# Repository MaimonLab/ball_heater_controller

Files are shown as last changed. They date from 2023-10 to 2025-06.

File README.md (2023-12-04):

# Ball Heater Controller

This repo contains the schematics and associated code for a controller to control the temperature of a ball holder or other device using closed loop PID drive of a resistive heater. There is a Python class to interact with the controller over USB-Serial, as well as a ROS2 Node to send and receive commands with the controller using ROS2.

For instructions on building a Ball Heater Controller, see [Assembly.](docs/assembly.md)

## Basic Usage

The Ball Heater Controller can be used independently of a computer by simply supplying it with AC power and attaching a ball heater and thermistor assembly to the main 4 pin output port on the front.

You can then change the mode by pressing and holding the control knob (see [Modes](#controller-modes)), and set the temperature setpoint (shown lower left as `SP:` on the LCD) by turning the knob. Current temperature is shown bottom right on the LCD.

### Python

The device can also be used with a computer for greater control and temperature logging. Interaction is done over USB-Serial, and the computer side is managed through the `BallHeaterDriver` Python class found in [`ball_heater_driver.py`](ball_heater_controller/ball_heater_controller/ball_heater_driver.py). An example of how this class can be used can be found in the Jupyter Notebook [`ball_heater_controller_testing.ipynb`](ball_heater_controller/ball_heater_controller/ball_heater_controller_testing.ipynb)

In short, after creating a `BallHeaterDriver` object, providing the correct serial port, commands can be sent using the `send_command` method. The main commands you will use are `status`, `set_target_temp`, and `set_control_mode`. Valid syntax for creating an object and sending these commands is shown below, with the first valid serial port chosen by default.

```python
import ball_heater_driver 
from list_ports import list_ports
import time

ports = [
    port
    for port in list_ports()
    if port["manufacturer"] is not None and "Silicon Labs" in port["manufacturer"]
]
port = ports[0]["port"]
print(f"Using Port: {port}")
ball_heater = ball_heater_driver.BallHeaterDriver(port=port)

# wait for the device to reset
time.sleep(5)

# Get and print status
success, status = ball_heater.send_command('status', [])
print('current status is:')
print('\n'.join((f"{key} : {value}") for key, value in status.items()))

# Set the target temperature to 35 (will also set control mode to remote)
ball_heater.send_command("set_target_temp", [35])

# Set the control mode back to standby
ball_heater.send_command("set_control_mode", ["standby"])
```

### ROS2

There is also a ROS2 Node provided for interacting with the Ball Heater Controller, [`ball_heater_node.py`](ball_heater_controller/ball_heater_controller/ball_heater_node.py).  The launch file [example_ball_heater.launch.py](ball_heater_controller/launch/example_ball_heater.launch.py), along with the config file [example_config.yaml](ball_heater_controller/config/example_config.yaml) will launch the node, as well as an example client node that can interact with the ball_heater_node.  It will also launch the ball_heater_gui that will subscribe to and print the heater status, and let the user set the temperature setpoint.  Once installed, set the `serial_port` or `device_serial_number` in `example_config.yaml` and launch the launch file using

```bash
ros2 launch ball_heater_controller example_ball_heater.launch.py 
```

Generally, the `BallHeaterNode` must be given a `serial_port` or a `device_serial_number` to specify the controller. Then, the status information will be published to the `ball_heater_status_topic` (default `ball_heater_controller/status_topic`), and the temperature can be set by another node by publishing to the `ball_heater_set_temp_topic` (default `ball_heater_controller/set_temp_topic`)

## Sub-directories

* `ball_heater_controller` -- ROS2 Package with a Node to interact with and control the heater, as well as `ball_heater_driver.py` which contains a Python class `BallHeaterDriver` to interact with the controller.
* `ball_heater_controller_interfaces` -- ROS2 Package with custom message types associated with the above package.
* `ball_heater_controller_firmware` -- Firmware for the microcontroller at the center of the PCB.
* `ball_heater_controller_pcb` -- Design files and gerbers for the printed circuit board for the Ball Heater Controller.
* `ball_heater_controller_case` -- Vector files for laser cuttting the case for the Ball Heater Controller.
* `docs` -- Additional documentation.

## Controller Modes

The controller has several different modes, shown upper left on the LCD display, and its behavior will be different depending on what mode it is in. The mode can be changed using the `set_control_mode` command through the interface, or by pressing and holding the control knob on the front of the device for >= 1 second.

* **Standby** On startup, the controller will be in standby mode, and the heater will not be driven, but the temperature will be shown on screen.
* **Local Control**  Pressing the control from standby mode will switch into `local control` mode, and the temperature setpoint can then be adjusted by turning the control knob.  This mode is useful for running the ball heater without a computer attached, or without needing to set the temp from the computer.
* **Remote Control** In this mode, the setpoint temperature is set from the computer using the `set_target_temp` command. Any `set_target_temp` commands received by the controller will automatically switch the controller into this mode.
* **Error Mode** There are also several error modes discussed below in [Safety Cutoffs](#safety-cutoffs--troubleshooting)

## Install

Run the installation script

```bash
./install_dependencies.sh
```

## Safety Cutoffs / Troubleshooting

The ball heater firmware has several different safety cutoffs built in that will trigger different errors and shut down the heater to prevent overheating. Once one of these error modes has been activated, the heater output will shut down, and the type of error will be displayed on the LCD. Pressing and holding the control knob down will reset the device into standby mode if the error state has been resolved.

1. **High temp error:** If the heater temperature sensor reads over 60 °C, the device will go into *High temp error* and shutdown.  
2. **No Temp Sensor:**  If the temperature sensor for the ball heater is not detected because it has been unpluged or a wire has broken, the device will go into *No Temp Sensor Error* and shutdown. When the sensor is replaced, the device will return to standby mode. Note that this is only for the integrated temp sensor in the ball heater, not the optional aux temp sensor.
3. **Heater Non Responsive:** If the control loop drives the  heater at a high power for too long, eg if the temperature is not responding properly, the device will go into *Heater Non Responsive* error and shutdown.

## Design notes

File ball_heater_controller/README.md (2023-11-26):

# ball_heater

ROS2 package for the Ball Heater Controller

# Dependencies
<!-- 
# Example

To test the ball_heater installation and communcation you can run:

    ros2 launch ball_heater example_ball_heater.launch.py

This will launch the example client and the eternarig_driver_node. To specify a specific device, you need to provide either the `device_serial_number` or the `device_port` parameter to the `ball_heater` in the `config/example_config.yaml` (the device_serial_number takes precedence). **If neither device serial number or device port are specified, a mock device is used that does not return status updates and throws errors when trying to publish status.**

# Finding device_serial_number

Each serial port device has a device_serial number. To list all serial port devices you can run the script:

    ros2 run light_sugar_driver list_ports -->

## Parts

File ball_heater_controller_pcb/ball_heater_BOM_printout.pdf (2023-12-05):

ball_heater_printout

Surface Mount Parts

References | | Description | Value
| 6 | 0805 SMD Capacitor | 0.1uF
C5 | 1 | 0805 SMD Capacitor | 2.2uF
C3 C4 | 2 | 0805 SMD Capacitor | 4.7uF
C2 C12 | 2 | 0805 SMD Capacitor | 10uF
D1 | 1 | Diode | S1G
J3 J4 | 2 | JST PH 3 pin vertical | B3B-PH-SM4-TB
J2 | 1 | JST SH 4 pin vertical | qwiic
Q1 | 1 | MOSFET 2N-CH 50V 0.2A SC70-6 | BSS138DW-7-F
Q2 | 1 | MOSFET N-CH 60V 115MA SOT-23 | TSM170N06CP
R2 | 1 | 0805 SMD Resistor | 10R
R1 R5 R6 | 3 | 0805 SMD Resistor | 10k
R3 R4 | 2 | 0805 SMD Resistor | 10k 1%
RN1 RN2 | 2 | | 10k
SW2 | 1 | SMD DPST switch | CL-SB-12A-01T

Through Hole Parts

References | | Description | Value
A1 | 2 | 14 position female headers
A1 | 1 | Metro Mini | Arduino_UNO_R3
C1 | 1 | TH Capacitor 12.5 by 5mm pitch | 470uF
J6 | 1 | DC Barrel Jack
J5 | 1 | M8 4 pin connector | M8S-04PFFR-SF8001
J1 | 1 | Screw Terminal, 2 pos | Screw_Terminal_01x02
PS1 | 1 | 5V to 12V DC-DC PSU | F0512S-1WR3
SW1 | 1 | | RotaryEncoder_Switch

Quantity
Per PCB
C6 C7 C8 C9
C10 C11

4 resistor network, parallel topology, split

Quantity
Per PCB

Rotary encoder, dual channel, incremental quadrate outputs, with switch

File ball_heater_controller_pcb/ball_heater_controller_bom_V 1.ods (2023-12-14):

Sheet: ball_heater_BOM
References | Quantity Per PCB | Description | Value | part number | digikey link
A1 | 1 | Metro Mini | Arduino_UNO_R3 | 2590 | https://www.adafruit.com/product/2590
C6 C7 C8 C9 C10 C11 | 6 | 0805 SMD Capacitor | 0.1uF | 311-1140-1-ND | https://www.digikey.com/en/products/detail/yageo/CC0805KRX7R9BB104/302874
C5 | 1 | 0805 SMD Capacitor | 2.2uF | 490-14467-1-ND | https://www.digikey.com/en/products/detail/murata-electronics/GRM21BR71E225KE11L/6606096
C3 C4 | 2 | 0805 SMD Capacitor | 4.7uF | 1276-1244-1-ND | https://www.digikey.com/en/products/detail/samsung-electro-mechanics/CL21A475KAQNNNE/3886902
C2 C12 | 2 | 0805 SMD Capacitor | 10uF | 1276-2891-1-ND | https://www.digikey.com/en/products/detail/samsung-electro-mechanics/CL21A106KAYNNNE/3888549
C1 | 1 | TH Capacitor 12.5 by 5mm pitch | 470uF | 493-12789-1-ND | https://www.digikey.com/en/products/detail/nichicon/UVR1H471MHD1TO/4328413
D1 | 1 | Diode | S1G | S1G-FDICT-ND | https://www.digikey.com/en/products/detail/diodes-incorporated/S1G-13-F/815936
J3 J4 | 2 | JST PH 3 pin vertical | B3B-PH-SM4-TB(LF)(SN) | 455-B3B-PH-SM4-TBCT-ND | https://www.digikey.com/en/products/detail/jst-sales-america-inc/B3B-PH-SM4-TB/926642?lang=en&site=us&x=-1041&y=-74
J6 | 1 | DC Barrel Jack |  | CP-002A-ND | https://www.digikey.com/en/products/detail/cui-inc/PJ-002A/96962
J5 | 1 | M8 4 pin connector | M8S-04PFFR-SF8001 | 1754-1451-ND | https://www.digikey.com/en/products/detail/amphenol-ltw/M8S-04PFFR-SF8001/7618868
J1 | 1 | Screw Terminal, 2 pos | Screw_Terminal_01x02 | 277-1247-ND | https://www.digikey.com/en/products/detail/phoenix-contact/1729128/260615
J2 | 1 | JST SH 4 pin vertical | qwiic | 455-BM04B-SRSS-TBCT-ND | https://www.digikey.com/en/products/detail/jst-sales-america-inc/BM04B-SRSS-TB/926696?lang=en&site=us&x=-1041&y=-74
PS1 | 1 | 5V to 12V DC-DC PSU | F0512S-1WR3 | 2725-F0512S-1WR3-ND | https://www.digikey.com/en/products/detail/mornsun-america-llc/F0512S-1WR3/13168056
Q1 | 1 | MOSFET 2N-CH 50V 0.2A SC70-6 | BSS138DW-7-F | BSS138DWQ-7DICT-ND | https://www.digikey.com/en/products/detail/diodes-incorporated/BSS138DWQ-7/6187221
Q2 | 1 | MOSFET N-CH 60V 115MA SOT-23 | TSM170N06CP | TSM170N06CPROGCT-ND | https://www.digikey.com/en/products/detail/taiwan-semiconductor-corporation/TSM170N06CP-ROG/7360167
R2 | 1 | 0805 SMD Resistor | 10R | P10.0CCT-ND | https://www.digikey.com/en/products/detail/panasonic-electronic-components/ERJ-6ENF10R0V/110893
R1 R5 R6 | 3 | 0805 SMD Resistor | 10k | 311-10.0KCRCT-ND | https://www.digikey.com/en/products/detail/yageo/RC0805FR-0710KL/730482
R3 R4 | 2 | 0805 SMD Resistor | 10k 1% | 311-10.0KCRCT-ND | https://www.digikey.com/en/products/detail/yageo/RC0805FR-0710KL/730482
RN1 RN2 | 2 | 4 resistor network, parallel topology, split | 10k | YC324J-10KCT-ND | https://www.digikey.com/en/products/detail/yageo/YC324-JK-0710KL/1005309
SW2 | 1 | SMD DPST switch | CL-SB-12A-01T | 563-1314-1-ND | https://www.digikey.com/en/products/detail/nidec-components-corporation/CL-SB-12A-01T/3507814
SW1 | 1 | Rotary encoder, dual channel, incremental quadrate outputs, with switch | RotaryEncoder_Switch | PEC09-2320F-S0015-ND | https://www.digikey.com/en/products/detail/bourns-inc/PEC09-2320F-S0015/2440328
Additional Parts
Digikey | Quantity Per PCB | Description | Value | part number | link
 | 2 | 14 position female headers |  | S7047-ND | https://www.digikey.com/en/products/detail/sullins-connector-solutions/PPPC141LFBN-RC/810186
 | 1 | Thermistor | 10k ohm | 495-2149-ND | https://www.digikey.com/en/products/detail/epcos-tdk-electronics/B57863S0103F040/739899
 | 1 | Rocker Switch DPST 20A (AC) 125 V Panel Mount, Snap-In |  | EG1531-ND | https://www.digikey.com/en/products/detail/e-switch/R5BBLKREDFF1/301978
 | 1 | Enclosed AC DC Converters 1 Output 5V 85 ~ 264 VAC, 120 ~ 373 VDC Input |  | 1866-3318-ND | https://www.digikey.com/en/products/detail/mean-well-usa-inc/LRS-100-5/7705010?lang=en&site=us&x=-1041&y=-74
 | 1 | Power Entry Connector Receptacle, Male Blades - Module IEC 320-C14 Panel Mount, Flange |  | Q203-ND | https://www.digikey.com/en/products/detail/qualtek/719W-00-04/245544
 | 1 | M8 4 pin cable |  | A127849-ND | https://www.digikey.com/en/products/detail/te-connectivity-amp-connectors/1-2273002-3/5399319
McMasterCarr | Quantity Per Heater | Description | Value | part number | link
 | 4 | Female Threaded Hex Standoff Aluminum, 1/4" Hex, 1" Long, 6-32 Thread |  | 91780A133 | https://www.mcmaster.com/91780a133
 | 20 | 18-8 Stainless Steel Button Head Hex Drive Screws Black-Oxide, 6-32 Thread Size, 1/2" Long |  | 97763A143 | https://www.mcmaster.com/97763A143/
 | 12 | 18-8 Stainless Steel Hex Nut Black-Oxide, 6-32 Thread Size |  | 96537A130 | https://www.mcmaster.com/96537A130/
 | 9 inches | Easy-to-Form Nickel Chromium Alloy 0.025 Diameter x 69 Feet Long, 1/8 lb. Spool |  | 8880K77 | https://www.mcmaster.com/8880K77/
 | 4 inches | Super-Thin Masking Tape for Electronics 1/2" Wide, 108 Feet Long |  | 1754N12 | https://www.mcmaster.com/1754N12/
 | 1 | Clear Scratch- and UV-Resistant Acrylic Sheet 12" x 24" x 1/8" |  | 8589K42 | https://www.mcmaster.com/8589K42/
 | 1 | Clear Scratch- and UV-Resistant Acrylic Sheet 12" x 24" x ¼" |  | 8589K82 | https://www.mcmaster.com/8589K82/
Adafruit | Quantity Per PCB | Description | Value | part number | link
 | 1 | USB C panel mount extension |  | 4218 | https://www.adafruit.com/product/4218
 | 1 | Machined Knob |  | 2056 | https://www.adafruit.com/product/2056

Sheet: ball_heater_printout
Surface Mount Parts
 | References | Quantity Per PCB | Description | Value
 | C6 C7 C8 C9 C10 C11 | 6 | 0805 SMD Capacitor | 0.1uF
 | C5 | 1 | 0805 SMD Capacitor | 2.2uF
 | C3 C4 | 2 | 0805 SMD Capacitor | 4.7uF
 | C2 C12 | 2 | 0805 SMD Capacitor | 10uF
 | D1 | 1 | Diode | S1G
 | Q1 | 1 | MOSFET 2N-CH 50V 0.2A SC70-6 | BSS138DW-7-F
 | Q2 | 1 | MOSFET N-CHANNEL 60V 38A TO252 | TSM170N06CP
 | R2 | 1 | 0805 SMD Resistor | 10R
 | R1 R5 R6 | 3 | 0805 SMD Resistor | 10k
 | R3 R4 | 2 | 0805 SMD Resistor | 10k 1%
 | RN1 RN2 | 2 | 4 resistor array, parallel topology, split | 10k
 | SW2 | 1 | SMD DPST switch | CL-SB-12A-01T
 | J3 J4 | 2 | JST PH 3 pin vertical | B3B-PH-SM4-TB
 | J2 | 1 | JST SH 4 pin vertical | qwiic
Through Hole Parts
 | References | Quantity Per PCB | Description | Value
 | A1 | 2 | 14 position female headers
 | A1 | 1 | Metro Mini | Arduino_UNO_R3
 | C1 | 1 | TH Capacitor 12.5 by 5mm pitch | 470uF
 | J6 | 1 | DC Barrel Jack
 | J5 | 1 | M8 4 pin connector | M8S-04PFFR-SF8001
 | J1 | 1 | Screw Terminal, 2 pos | Screw_Terminal_01x02
 | PS1 | 1 | 5V to 12V DC-DC PSU | F0512S-1WR3
 | SW1 | 1 | Rotary encoder, dual channel, incremental quadrate outputs, with switch | RotaryEncoder_Switch

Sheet: ball_heater_controller_bom_V 1
Component | Description | Part | References | Value | Footprint | Quantity Per PCB | Datasheet | Category | DK_Datasheet_Link | DK_Detail_Page | Digi-Key_PN | Family | MPN | Manufacturer | Status | Field4 | Field5 | Field6 | Field7 | Field8 | MANUFACTURER | MAXIMUM_PACKAGE_HEIGHT | PARTREV | STANDARD
1 |  | Arduino_UNO_R3-MCU_Module | A1 | Arduino_UNO_R3 | Metro_mini | 1 | https://www.arduino.cc/en/Main/arduinoBoardUno
2 | Unpolarized capacitor | C | C6 C7 C8 C9 C10 C11 | 0.1uF | C_0805_2012Metric_Pad1.18x1.45mm_HandSolder | 6 | ~
3 | Unpolarized capacitor | C | C5 | 2.2uF | C_0805_2012Metric_Pad1.18x1.45mm_HandSolder | 1 | ~
4 | Unpolarized capacitor | C | C3 C4 | 4.7uF | C_0805_2012Metric_Pad1.18x1.45mm_HandSolder | 2 | ~
5 | Unpolarized capacitor | C | C2 C12 | 10uF | C_0805_2012Metric_Pad1.18x1.45mm_HandSolder | 2 | ~
6 |  | CP1-Device | C1 | 470uF | CP_Radial_D12.5mm_P5.00mm | 1
7 | DIODE GEN PURP 400V 1A SMA | S1G | D1 | S1G | DO-214AC | 1 | https://www.onsemi.com/pub/Collateral/S1M-D.pdf | Discrete Semiconductor Products | https://www.onsemi.com/pub/Collateral/S1M-D.pdf | /product-detail/en/on-semiconductor/S1G/S1GFSCT-ND/965720 | S1GFSCT-ND | Diodes - Rectifiers - Single | S1G | ON Semiconductor | Active
8 |  | B3B-PH-SM4-TB(LF)(SN) | J3 J4 | B3B-PH-SM4-TB(LF)(SN) | JST_PH_B3B-PH-SM4-TB_1x03-1MP_P2.00mm_Vertical | 2 | https://www.digikey.com/product-detail/en/jst-sales-america-inc/B3B-PH-SM4-TB_LF__SN_/455-1735-1-ND/926832 |  |  |  |  |  |  |  |  | B3B-PH-SM4-TB_LF__SN_ | PH Series 3 Position 2 mm Pitch Crimp Surface Mount Top Entry Shrouded Header | 2010 JST | JST Sales | 455-1735-1-ND
9 | DC Barrel Jack with an internal switch | Barrel_Jack_Switch | J6 | Barrel_Jack_Switch | BarrelJack_Horizontal | 1 | ~
10 |  | M8S-04PFFR-SF8001 | J5 | M8S-04PFFR-SF8001 | AMPHENOL_M8S-04PFFR-SF8001 | 1 |  |  |  |  |  |  |  |  |  |  |  |  |  |  | Amphenol | 12.581 mm | B | Manufacturer Recommendations
11 | Generic screw terminal, single row, 01x02, script generated (kicad-library-utils/schlib/autogen/connector/) | Screw_Terminal_01x02 | J1 | Screw_Terminal_01x02 | Term_Block_1x2_P5.08MM | 1 | ~
12 | Generic connector, single row, 01x04, script generated (kicad-library-utils/schlib/autogen/connector/) | Conn_01x04_Male | J2 | qwiic | BM04B-SRSS-TB(LF)(SN) | 1 | ~
13 |  | F0512S-1WR3 | PS1 | F0512S-1WR3 | CONV_F0512S-1WR3 | 1 |  |  |  |  |  |  |  |  |  |  |  |  |  |  | Mornsun | 10.16 mm | 2021.12.28-A/6 | Manufacturer Recommendations
14 | MOSFET 2N-CH 50V 0.2A SC70-6 | BSS138DW-7-F | Q1 | BSS138DW-7-F | SOT-363 | 1 | https://www.diodes.com/assets/Datasheets/ds30203.pdf | Discrete Semiconductor Products | https://www.diodes.com/assets/Datasheets/ds30203.pdf | /product-detail/en/diodes-incorporated/BSS138DW-7-F/BSS138DW-FDICT-ND/808541 | BSS138DW-FDICT-ND | Transistors - FETs, MOSFETs - Arrays | BSS138DW-7-F | Diodes Incorporated | Active
15 | MOSFET N-CH 60V 115MA SOT-23 | TSM170N06CP | Q2 | TSM170N06CP | TO-252-3 | 1 | https://www.taiwansemi.com/assets/uploads/datasheet/TSM170N06_B15.pdf | Discrete Semiconductor Products | https://www.taiwansemi.com/assets/uploads/datasheet/TSM170N06_B15.pdf | /products/detail/taiwan-semiconductor-corporation/TSM170N06CP-ROG/7360167 | TSM170N06CPROGCT-ND | Transistors - FETs, MOSFETs - Single | TSM170N06CP | Taiwan Semiconductor | Active
16 | Resistor, US symbol | R_US | R2 | 10R | R_0805_2012Metric_Pad1.20x1.40mm_HandSolder | 1 | ~
17 | Resistor, US symbol | R_US | R1 R5 R6 | 10k | R_0805_2012Metric_Pad1.20x1.40mm_HandSolder | 3 | ~
18 | Resistor, US symbol | R_US | R3 R4 | 10k 1% | R_0805_2012Metric_Pad1.20x1.40mm_HandSolder | 2 | ~
19 | 4 resistor network, parallel topology, split | R_Pack04_Split | RN1 RN2 | 10k | R_Array_Convex_4x1206 | 2 | ~
20 |  | CL-SB-12A-01T | SW2 | CL-SB-12A-01T | CL-SB-12A-01T | 1 | CL-SB-12A-01T
21 | Rotary encoder, dual channel, incremental quadrate outputs, with switch | RotaryEncoder_Switch | SW1 | RotaryEncoder_Switch | RotaryEncoder_Bourns_Horizontal_PEC09-2xxxF-Sxxxx | 1 | ~
Component Groups: | 21
Component Count: | 33
Fitted Components: | 33
Number of PCBs: | 1
Total components: | 33
Schematic Version: | V 1
Schematic Date: | 2023-10-19
PCB Variant: | default
BoM Date: | 2023 December 05, Tuesday 11:02:49
Schematic Source: | ball_heater_controller.kicad_sch
KiCad Version: | Eeschema 7.0.8

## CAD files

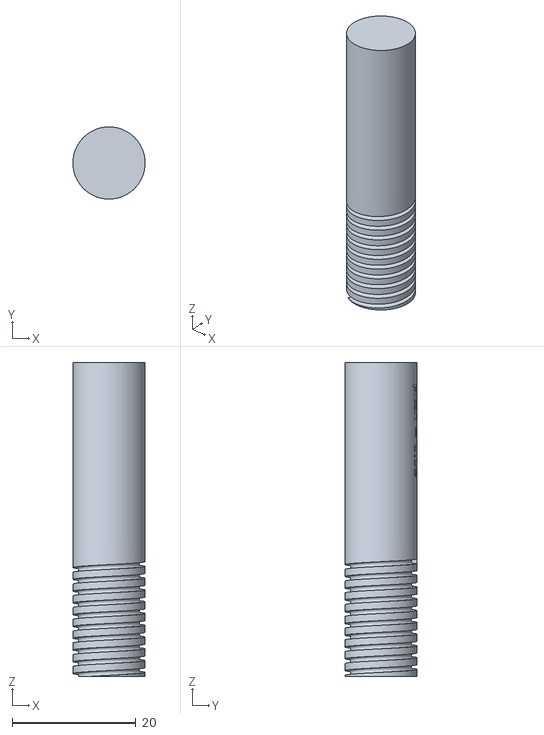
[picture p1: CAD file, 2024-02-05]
docs/ball_heater_guide-01.stl
11.7 x 11.7 x 50.8

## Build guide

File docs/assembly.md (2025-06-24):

# Ball Heater Controller Assembly

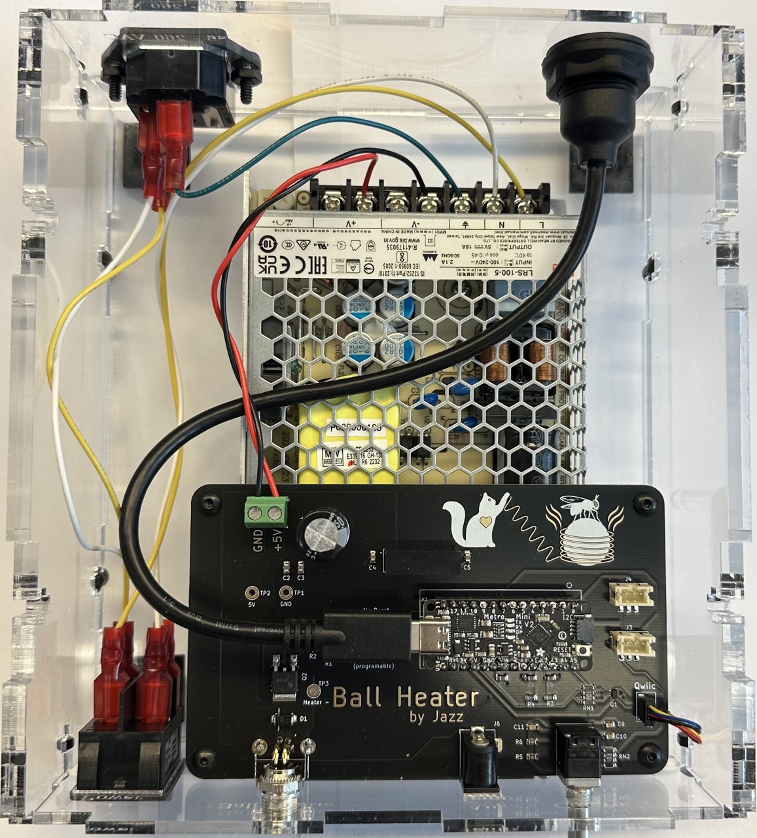
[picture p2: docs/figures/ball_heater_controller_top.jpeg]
controller top view


The parts needed to build the ball heater are listed with links and part numbers in the first sheet of the [Bill of Materials (BOM)](../ball_heater_controller_pcb/ball_heater_controller_bom_V%201.ods) spreadsheet.

## PCB

PCBs can be ordered from one of many PCB supply houses, eg [pcbway](pcbway.com) or [jlcpcb](https://jlcpcb.com), using the [zipped gerber files](../ball_heater_controller_pcb/ball_heater_controller_v1.zip). Order a stencil as well to make the surface mount assembly easier and faster.

Once PCBs and parts have been acquired, apply solder paste using the stencil, and then use the [BOM printout](../ball_heater_controller_pcb/ball_heater_BOM_printout.pdf) to place surface mount parts in the correct locations matching their reference designators.  Then reflow the solder paste using a reflow over or hot air rework system. Lastly, solder the through hole components.

## Enclosure

Laser cut the two enclosure parts files out of 1/8 inch and 1/4 inch acrylic for [ball_heater_box_eighth](../ball_heater_controller_enclosure/tall_enclosure/ball_heater_box_eighth.ai) and [ball_heater_box_quarter](../ball_heater_controller_enclosure/tall_enclosure/ball_heater_box_quarter.ai), respectively. The case is assembled with 1/2 inch long #6-32 button head screws and nuts in the T-slots.

## Putting it all together

* Cut and prepare wires. Strip 1cm on all ends, and crimp 1/4 inch quick disconnect terminals as specified.

| Use |  Colors | Length | End Treatment|
|---|---|---| --- |
|Power in ground|green |5 inches | crimp one end|
|Power in to switch| yellow + white | 4 inches | crimp both ends|
|Switch to PSU| yellow + white | 8 inches | crimp one end|
|PSU to board| black + red | 4 inches | strip only|

* Attach wires to switch, power in on the bottom, power to PSU on the top, whith white on one  side and yellow on the other.
* Install switch into front panel.
* Attach USB panel mount cable to back panel.
* Attach IEC C14 power inlet to back panel with 6-32 by 5/8 flat head screws and nuts.
* Screw PSU to bottom of case with M3 x 8mm button head screws.
* Put rubber feet on bottom of case.
* Attach 4 in QWIIC cable to LCD.
* Screw LCD to front of case with #2-56 by 1/2 inch screws, nuts and washers, using acrylic spacer between LCD and front panel.
* Put the 4 walls and on case.
* Attach 4 1.5 inch 6-32 standoffs to board with 6-32 by 3/8 inch button head screws.
* Remove green O ring from the M8 connector on the PCB
* Attach board to case bottom with more  6-32 by 3/8 inch button head screws.
* Attach wires from switch to power inlet. Yellow to L and white to N.
* Attach green ground wire from power inlet to PSU ground terminal (⏚).
* Attach wires from switch to PSU. Yellow to L and white to N.
* Attach wires from PSU to board, red between V+ on PSU and +5V terminal on board, black from V- to GND on board. Trim stripped end slightly shorter before securing to board if bare wire shows outside the screw terminal.
* Make sure that the switch (SW2) to the left of the microcontroller is in the down position, towards "Normal Reset"

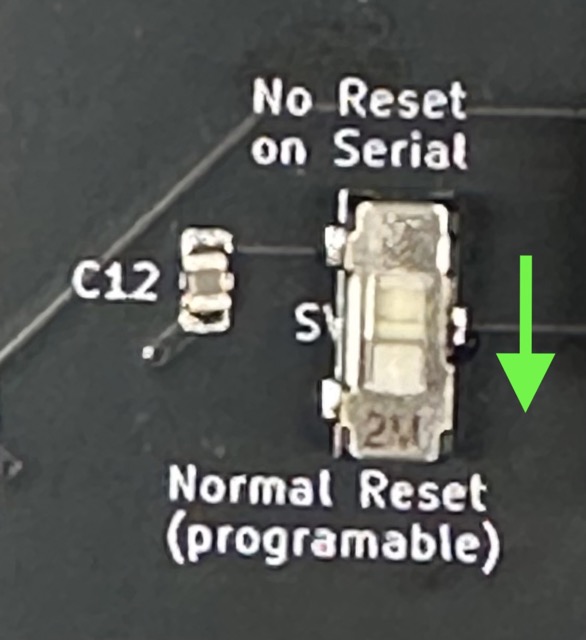
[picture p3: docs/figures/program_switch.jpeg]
switch position


* Attach USB c cable to the microcontroller on the PCB.
* Screw box together with 6-32 by 1/2 inch button head screws and nuts.
* Loosen screws holding the PCB to the box, slide PCB till it is flush against the front panel, and re-tighten.
* Screw washer and nut onto rotary encoder and nut onto M8 connector on front of box.
* Put a 1 A fuse in the fuse holder of the power inlet.
* Put knob onto the rotary encoder.
* Program the microcontroller with the code from [`ball_heater_controller_firmware`](../ball_heater_controller_firmware/ball_heater_controller_firmware.ino) using the Arduino IDE, and test!

## Ball Heater

The ball heater itself is made by wrapping the bottom end of an aluminum ball holder in a layer of kapton tape for electrical insulation, and then a helix of nichrome wire for heating as well as a thermistor for temperature sensing.  All of this is secured and made a thermal unit using thermally conductive epoxy.

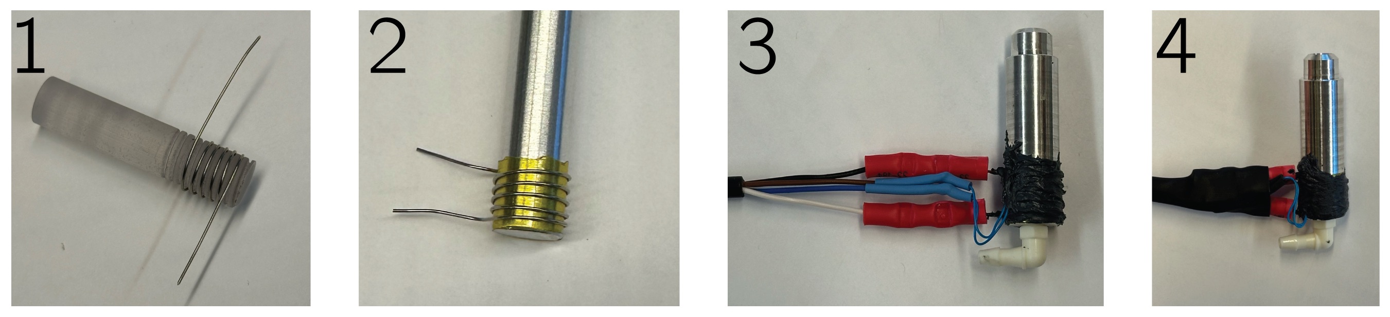
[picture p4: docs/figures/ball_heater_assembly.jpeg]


1. Start with 9.5 in of [nichrome wire](https://www.mcmaster.com/8880K77/) and wrap into a helix on a 3d printed [mandrel.](ball_heater_guide-01.stl)
2. Cover the bottom of the ball heater with 1 layer of [kapton tape](https://www.mcmaster.com/1754N12/), and then put the nichrome helix over it by gently unwinding it as it goes on. It should fit tight.  Make sure the coils are evenly spaced and none are touching or touching the aluminum. Screw in the [90 degree hose barb](https://www.mcmaster.com/5463K54/), if using, so that you can align the wires with it.
3. Cover the Nichrome helix with [thermal epoxy](https://www.digikey.com/en/products/detail/mg-chemicals/8329TCM-6ML/6035511), and add a [thermistor](https://www.digikey.com/en/products/detail/epcos-tdk-electronics/B57863S0103F040/739899) just above the nichrome. It should be touching the aluminum, with the wires going down over the nichrome. Cover with thermal epoxy. You will need about 1 gram of thermal epoxy per heater that you are making, mix a bit extra as well.

### Wiring

The heater is wired using a 4-pin M8 cable as follows :

|Wire Color | Attachment |
| --- | ----|
|Black | Nichrome heater|
|White | Nichrome heater|
|Blue | Thermistor|
|Brown | Thermistor|

* Trim black and white wires ~1 cm shorter than blue/brown, and use butt splice crimps to connect the nichrome wire to the black and white wires (it doesn't matter which one is on top).
* Strip Blue/brown wires and add heat shrink to each.
* Solder one to each lead of the thermistor, making sure that there is slack so that they will not get pulled on.
* Use heatshrink to insulate solder joints. It should look like (3) above.
* Add large heatshrink over all to neaten and strengthen connection (4).

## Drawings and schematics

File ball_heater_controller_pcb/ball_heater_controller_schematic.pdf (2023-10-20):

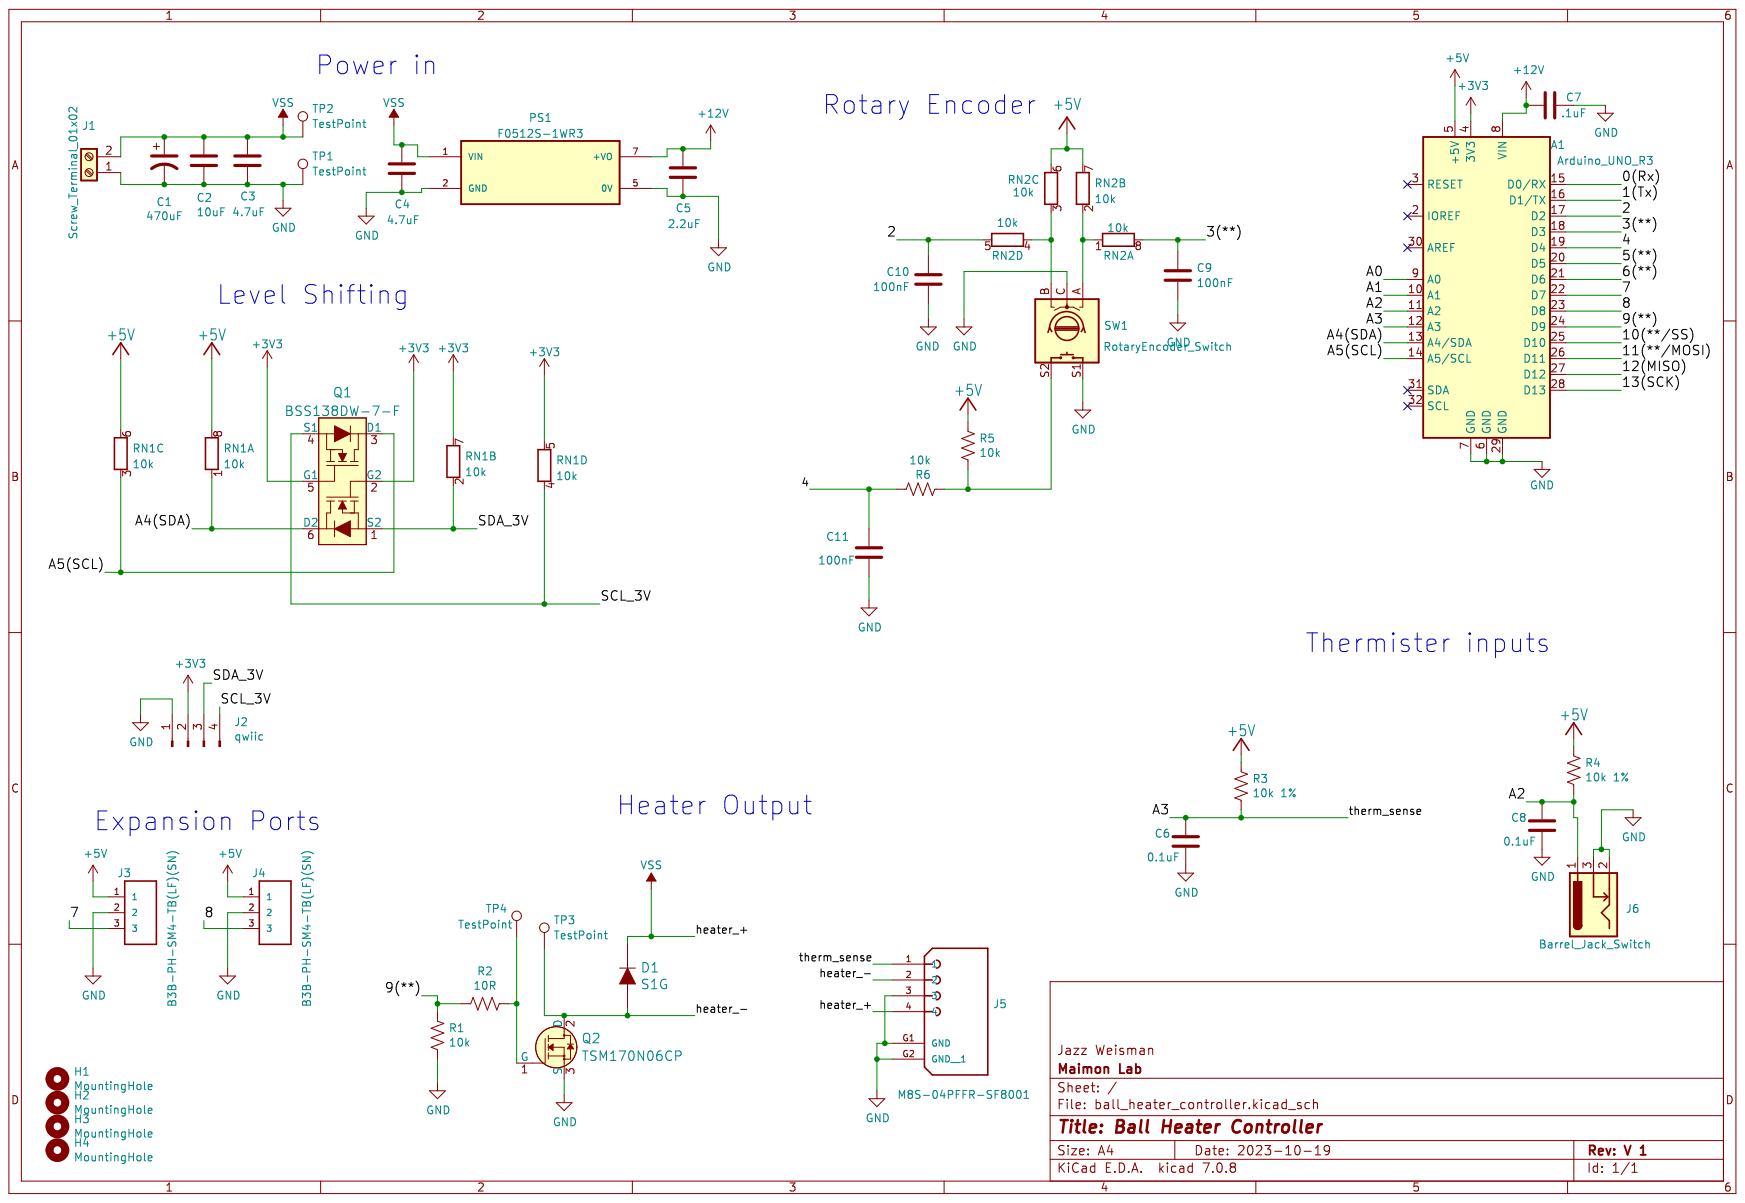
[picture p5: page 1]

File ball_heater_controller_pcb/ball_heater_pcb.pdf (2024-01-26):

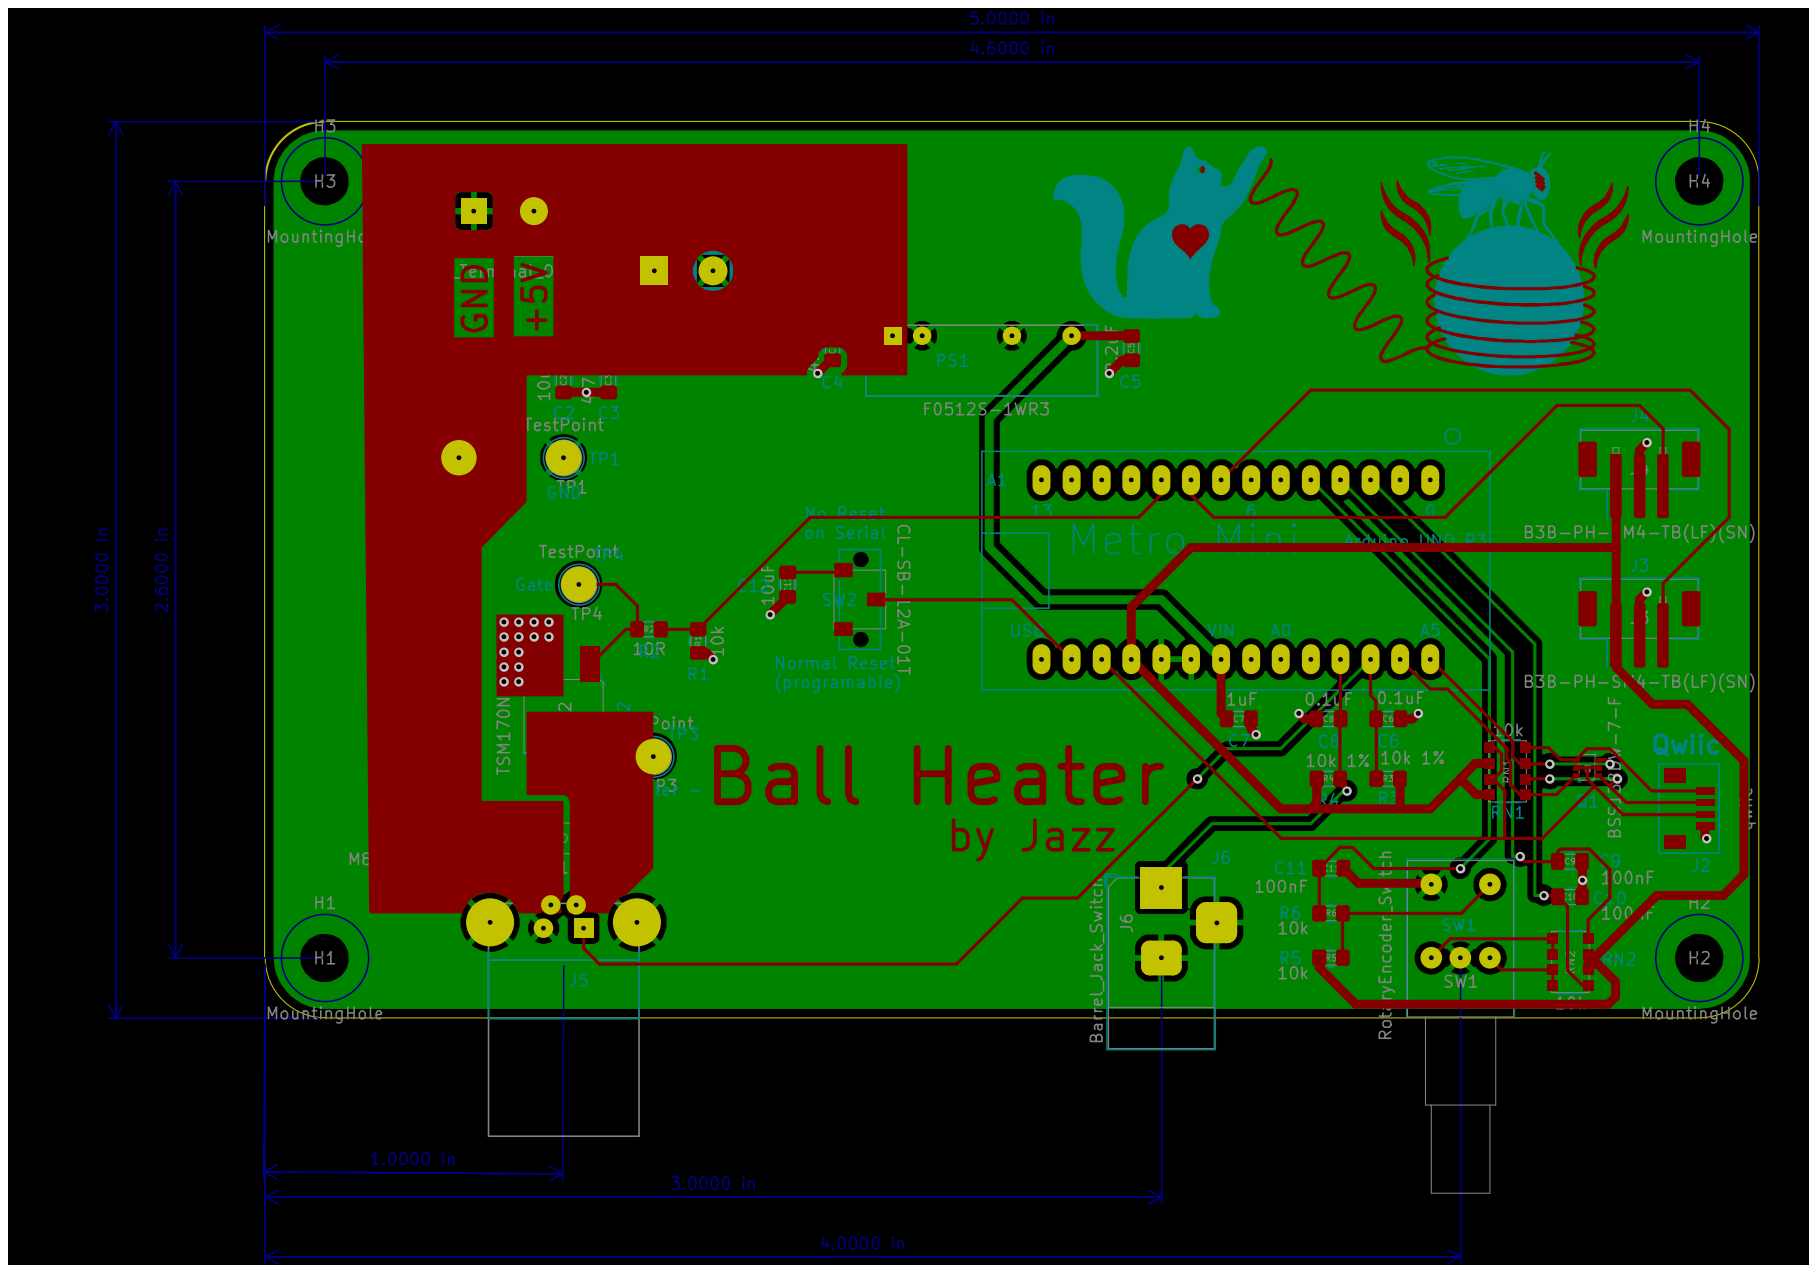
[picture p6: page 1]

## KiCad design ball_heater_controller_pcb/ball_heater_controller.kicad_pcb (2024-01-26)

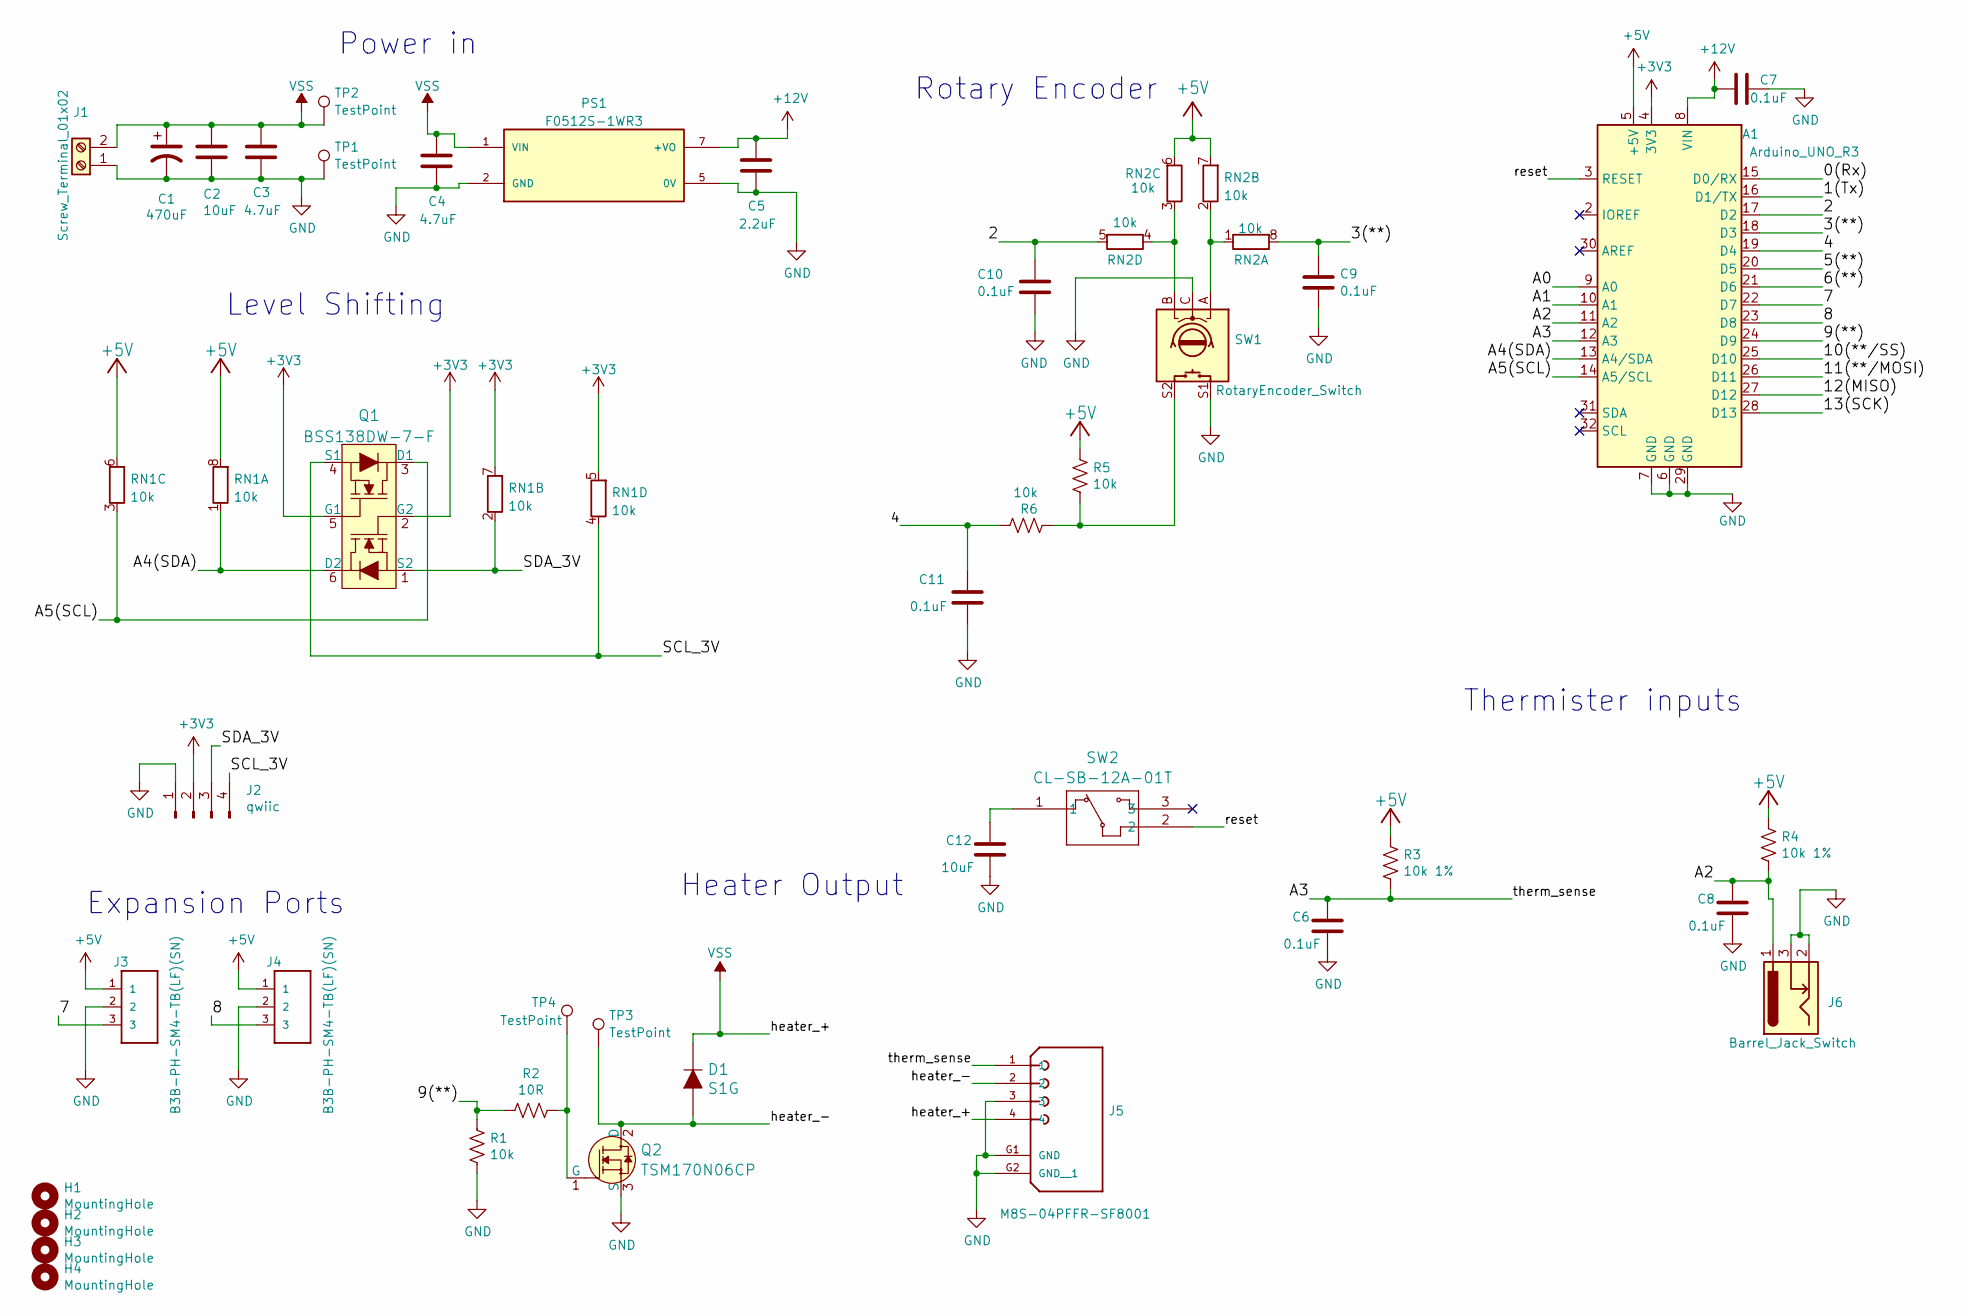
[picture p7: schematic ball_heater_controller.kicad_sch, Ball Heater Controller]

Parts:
A1: Arduino_UNO_R3; Metro_mini
C1: 470uF; CP_Radial_D12.5mm_P5.00mm
C2, C12: 10uF; C_0805_2012Metric_Pad1.18x1.45mm_HandSolder
C3, C4: 4.7uF; C_0805_2012Metric_Pad1.18x1.45mm_HandSolder
C5: 2.2uF; C_0805_2012Metric_Pad1.18x1.45mm_HandSolder
C6, C7, C8, C9, C10, C11: 0.1uF; C_0805_2012Metric_Pad1.18x1.45mm_HandSolder
D1: S1G; DO-214AC; MPN S1G; Digi-Key_PN S1GFSCT-ND
H1, H2, H3, H4: MountingHole; MountingHole_3.7mm
J1: Screw_Terminal_01x02; Term_Block_1x2_P5.08MM
J2: qwiic; BM04B-SRSS-TB(LF)(SN)
J3, J4: B3B-PH-SM4-TB(LF)(SN); JST_PH_B3B-PH-SM4-TB_1x03-1MP_P2.00mm_Vertical
J5: M8S-04PFFR-SF8001; AMPHENOL_M8S-04PFFR-SF8001; PARTREV B
J6: Barrel_Jack_Switch; BarrelJack_Horizontal
PS1: F0512S-1WR3; CONV_F0512S-1WR3; PARTREV 2021.12.28-A/6
Q1: BSS138DW-7-F; SOT-363; MPN BSS138DW-7-F; Digi-Key_PN BSS138DW-FDICT-ND
Q2: TSM170N06CP; TO-252-3; MPN TSM170N06CP; Digi-Key_PN TSM170N06CPROGCT-ND
R1, R5, R6: 10k; R_0805_2012Metric_Pad1.20x1.40mm_HandSolder
R2: 10R; R_0805_2012Metric_Pad1.20x1.40mm_HandSolder
R3, R4: 10k 1%; R_0805_2012Metric_Pad1.20x1.40mm_HandSolder
RN1, RN2: 10k; R_Array_Convex_4x1206
SW1: RotaryEncoder_Switch; RotaryEncoder_Bourns_Horizontal_PEC09-2xxxF-Sxxxx
SW2: CL-SB-12A-01T
TP1, TP2, TP3, TP4: TestPoint; TestPoint_Loop_D2.60mm_Drill1.6mm_Beaded

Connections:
+3V3: A1.4 (3V3), J2.2, Q1.2 (G2), Q1.5 (G1), RN1.5 (R4.2), RN1.7 (R2.2)
+5V: A1.5 (+5V), J3.1, J4.1, R3.1, R4.1, R5.1, RN1.6 (R3.2), RN1.8 (R1.2), RN2.6 (R3.2), RN2.7 (R2.2)
+12V: A1.8 (VIN), C5.1, C7.2, PS1.7 (+VO)
/0(Rx): A1.15 (D0/RX)
/1(Tx): A1.16 (D1/TX)
/2: A1.17 (D2), C10.1, RN2.5 (R4.2)
/3(**): A1.18 (D3), C9.1, RN2.8 (R1.2)
/4: A1.19 (D4), C11.1, R6.1
/5(**): A1.20 (D5)
/6(**): A1.21 (D6)
/7: A1.22 (D7), J3.3
/8: A1.23 (D8), J4.3
/9(**): A1.24 (D9), R1.2, R2.2
/10(**/SS): A1.25 (D10)
/11(**/MOSI): A1.26 (D11)
/12(MISO): A1.27 (D12)
/13(SCK): A1.28 (D13)
/A0: A1.9 (A0)
/A1: A1.10 (A1)
/A2: A1.11 (A2), C8.1, J6.1, R4.2
/A3: A1.12 (A3), C6.1, J5.1, R3.2
/A4(SDA): A1.13 (A4/SDA), Q1.6 (D2), RN1.1 (R1.1)
/A5(SCL): A1.14 (A5/SCL), Q1.3 (D1), RN1.3 (R3.1)
/SCL_3V: J2.4, Q1.4 (S1), RN1.4 (R4.1)
/SDA_3V: J2.3, Q1.1 (S2), RN1.2 (R2.1)
/heater_-: D1.A, J5.2, Q2.2 (D), TP3.1
/reset: A1.3 (RESET), SW2.2
GND: A1.6 (GND), A1.7 (GND), A1.29 (GND), C1.2, C2.2, C3.2, C4.2, C5.2, C6.2, C7.1, C8.2, C9.2, C10.2, C11.2, C12.2, J1.1, J2.1, J3.2, J4.2, J5.3, J5.G1 (GND), J5.G2 (GND__1), J6.2, J6.3, PS1.2 (GND), PS1.5 (0V), Q2.3 (S), R1.1, SW1.C, SW1.S1, TP1.1
unnamed: C12.1, SW2.1
unnamed: Q2.1 (G), R2.1, TP4.1
unnamed: R5.2, R6.2, SW1.S2
unnamed: RN2.1 (R1.1), RN2.2 (R2.1), SW1.A
unnamed: RN2.3 (R3.1), RN2.4 (R4.1), SW1.B
VSS: C1.1, C2.1, C3.1, C4.1, D1.K, J1.2, J5.4, PS1.1 (VIN), TP2.1

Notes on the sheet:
Power in
Heater Output
Thermister inputs
Expansion Ports
Rotary Encoder
Level Shifting

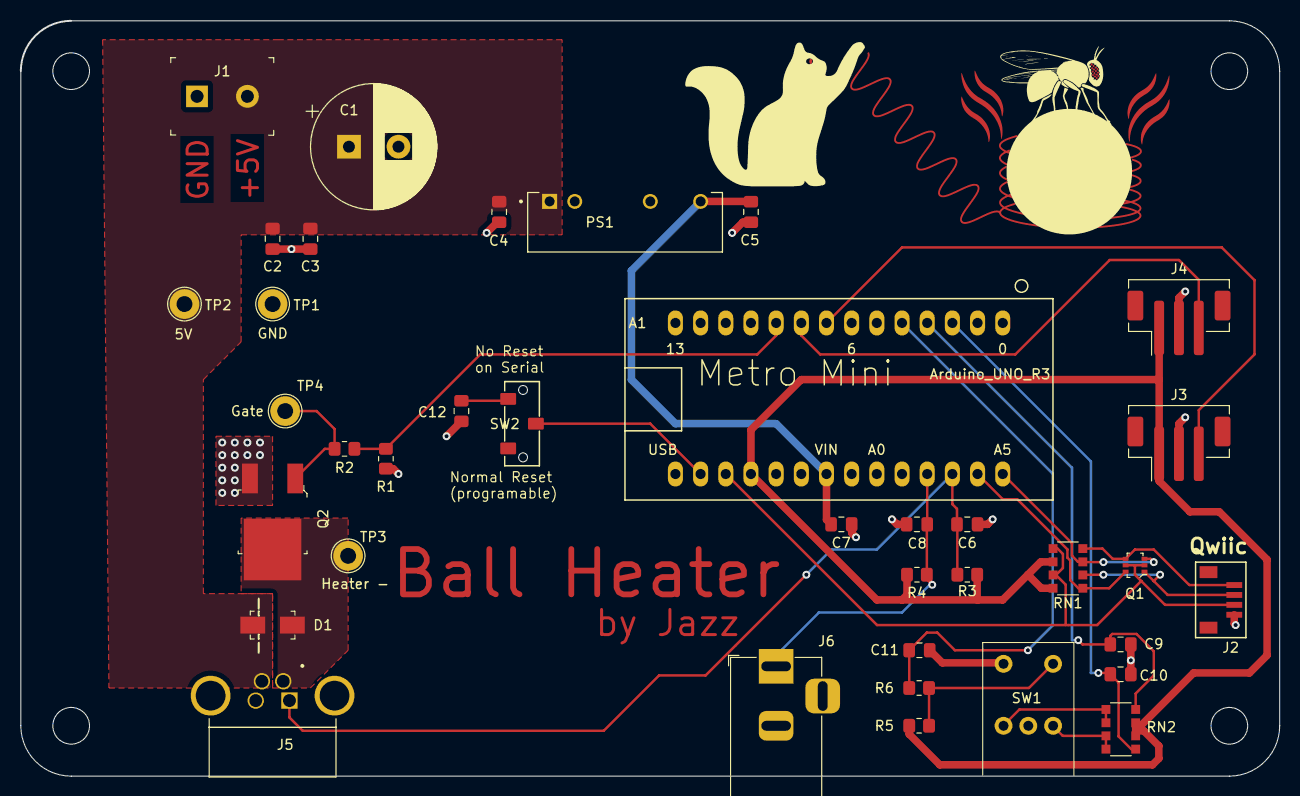
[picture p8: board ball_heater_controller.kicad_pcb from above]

Board: 2 copper layers, 127.0 x 76.2 mm, 41 parts (0 on the bottom side), 24 nets.

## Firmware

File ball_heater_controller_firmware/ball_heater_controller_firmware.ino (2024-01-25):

#include "Wire.h"
// #include "Adafruit_LiquidCrystal.h"
#include <Servo.h>
#include <Wire.h>
#include <Rotary.h>
// #include <hd44780.h> // main hd44780 header
// #include <hd44780ioClass/hd44780_I2Cexp.h> // i2c expander i/o class header
#include "BallHeater.h"
#include "SerialComms.h"
#include <PID_v1.h>
#include <avr/wdt.h>

#include <SerLCD.h> //Click here to get the library: http://librarymanager/All#SparkFun_SerLCD

// Pin Defines

// PIN	Assignment
// 0
// 1
// 2    rotary encoder B
// 3    rotary encoder A
// 4	rotary encoder switch (active low)
// 5
// 6
// 7    Expansion port J3
// 8    Expansion port J4
// 9    heater output
// 10
// 11
// 12
// 13
// A0
// A1
// A2   aux Thermistor
// A3   Thermistor main
// A4
// A5

#define ROTARY_1 2
#define ROTARY_2 3
#define ROTARY_SWITCH 4
#define SWITCH_HOLD_TIME 1000

#define TEMP_STEP 0.25F;

#define WIRECLOCK 400000L // tell hd44780 example to use this i2c clock rate

// hd44780_I2Cexp lcd; // declare lcd object: auto locate & auto config expander chip
SerLCD lcd; // Initialize the library with default I2C address 0x72

Rotary rotary = Rotary(ROTARY_1, ROTARY_2);

BallHeater ball_heater;
SerialComms serial_comms = SerialComms(&ball_heater);
int state = 0;
unsigned long timestamp = 0;
unsigned long switch_on_time = 0;
bool switch_on = false;
int last_control_mode = -1;
int current_control_mode = -1;

// Screen Buffer
char line0[17];
char line1[17];

char target_temp_buff[6];
char heater_temp_buff[6];

void setup()
{
    pinMode(5, OUTPUT);
    pinMode(7, OUTPUT);
    wdt_disable(); // Disable WDT

    // pinMode(2);
    // pinMode(3);
    Serial.begin(115200);
    Wire.begin();
    // lcd.begin(16, 2);
    lcd.begin(Wire);
    lcd.setFastBacklight(0, 0, 128); // Set backlight to dim blue
    lcd.setContrast(0);              // Set contrast. Lower to 0 for higher contrast.

    sprintf(line0, "Ball Heater");
    sprintf(line1, "V 0.1");
    update_display(1);
    delay(3000);
    wdt_enable(WDTO_4S); // Enable WDT with a timeout of 4 seconds

    //    Wire.setClock(WIRECLOCK);
    ball_heater.init();
}

/*-------------------- check_encoder -------------------------
      Checks if the rotary encoder has been turned and updates the values
      accordingly. Also checks the switch and changes the control mode.
 ---------------------------------------------------------*/
void check_encoder(void)
{
    // Check if the rotary switch is on and if it has been on for long enough
    if (digitalRead(ROTARY_SWITCH) == LOW)
    {
        if (!switch_on) // if the switch has just been turned on
        {
            switch_on = true;
            switch_on_time = millis();
        }
        // otherwise, if it's been on, check if it's been on long enough
        else if ((millis() - switch_on_time) > SWITCH_HOLD_TIME)
        {
            current_control_mode = ball_heater.get_control_mode();
            switch (current_control_mode)
            {
            case STANDBY:
                ball_heater.set_control_mode(LOCAL_CONTROL);
                break;

            case LOCAL_CONTROL:
            case REMOTE_CONTROL:
            case HIGH_TEMP_ERROR:
            case NO_TEMP_ERROR:
            case NON_RESPONSIVE_ERROR:
            case MANUAL_TEST:
                ball_heater.set_control_mode(STANDBY);
                break;
            }
            switch_on = false;
        }
    }
    else // if the switch is off, reset the switch_on flag
    {
        switch_on = false;
    }

    // Check if the rotary encoder has been turned, and do stuff if so
    unsigned char result = rotary.process();
    if (result == DIR_NONE)
        return;

    if (ball_heater.get_control_mode() == LOCAL_CONTROL)
    {
        float current_goal_temp = ball_heater.get_target_temp();

        if (result == DIR_CW)
        {
            current_goal_temp += TEMP_STEP;
        }
        else if (result == DIR_CCW)
        {
            current_goal_temp -= TEMP_STEP;
        }
        ball_heater.set_target_temp(current_goal_temp);
    }

    else if (ball_heater.get_control_mode() == MANUAL_TEST)
    {
        float current_pwm = ball_heater.get_pwm_float();
        float new_pwm;
        float max_pwm = 100;
        float min_pwm = 0;

        if (result == DIR_CW)
        {
            new_pwm = min(current_pwm + 2, max_pwm);
        }
        else if (result == DIR_CCW)
        {
            new_pwm = max(current_pwm - 2, min_pwm);
        }
        ball_heater.set_pwm(new_pwm);
    }
}

/*-------------------- mySetCursor -------------------------
      Moves cursor with given delay instead of the hardcoded
      50ms from the library.
 ---------------------------------------------------------*/
void mySetCursor(byte col, byte row, int delay_ms)
{
    int row_offsets[] = {0x00, 0x40, 0x14, 0x54};
    // keep variables in bounds
    // Explicitly cast numeric literals to type byte to avoid ESP32 and ESP8266 compile errors
    row = max((byte)0, row);              // row cannot be less than 0
    row = min(row, (byte)(MAX_ROWS - 1)); // row cannot be greater than max rows

    // send the commandset
    lcd.beginTransmission();
    lcd.transmit(SPECIAL_COMMAND); // Send special command character
    lcd.transmit(LCD_SETDDRAMADDR | (col + row_offsets[row]));
    lcd.endTransmission();
    delay(delay_ms);
} // setCursor

/*-------------------- update_display -------------------------
      Updates the display with current text buffers if the time is right.
 ---------------------------------------------------------*/
void update_display(int interval)
{
    digitalWrite(7, HIGH);
    if (millis() % interval == 0)
    {
        current_control_mode = ball_heater.get_control_mode();
        if (last_control_mode != current_control_mode)
        {
            last_control_mode = current_control_mode;
            switch (current_control_mode)
            {
            case STANDBY:
                lcd.setFastBacklight(0, 0, 200); // Set backlight to dim blue
                break;
            case LOCAL_CONTROL:
                lcd.setFastBacklight(255, 0, 0); // Set backlight to red
                break;
            case REMOTE_CONTROL:
                lcd.setFastBacklight(255, 0, 255); // Set backlight to purple
                break;
            case HIGH_TEMP_ERROR:
            case NO_TEMP_ERROR:
            case NON_RESPONSIVE_ERROR:
                lcd.setFastBacklight(255, 200, 0); // Set backlight to yellow
                break;
            }
        }
        // lcd.setCursor(0, 0);
        mySetCursor(0, 0, 5);
        lcd.print(line0);
        // lcd.clear();
        // lcd.print(strcat(line0, line1));
        // lcd.setCursor(0, 1);
        mySetCursor(0, 1, 5);
        lcd.print(line1);
    }
    digitalWrite(7, LOW);
}

String get_control_mode_string(byte mode)
{
    switch (mode)
    {
    case STANDBY:
        return "Standby";
    case LOCAL_CONTROL:
        return "Local";
    case REMOTE_CONTROL:
        return "Remote";
    case MANUAL_TEST:
        return "Manual";
    case HIGH_TEMP_ERROR:
        return "High Temp Error";
    case NO_TEMP_ERROR:
        return "No Temp Sensor";
    case NON_RESPONSIVE_ERROR:
        return "Non Response ERR";
    default:
        return "Error";
    }
}

void loop()
{
    wdt_reset(); // Reset WDT
    check_encoder();
    ball_heater.tick();
    serial_comms.tick();

    String control_mode_string = get_control_mode_string(ball_heater.get_control_mode());
    float target_temp = ball_heater.get_target_temp();
    float heater_temp = ball_heater.get_heater_temp();
    dtostrf(target_temp, 4, 2, target_temp_buff);
    dtostrf(heater_temp, 4, 2, heater_temp_buff);

    digitalWrite(5, HIGH);

    snprintf(line0, 17, "%s. %3d pwm      ",
             control_mode_string.c_str(),
             round(ball_heater.get_pwm_float()));

    snprintf(line1, 17, "SP:%s C:%s",
             String(target_temp_buff).substring(0, 5).c_str(),
             String(heater_temp_buff).substring(0, 5).c_str());

    digitalWrite(5, LOW);

    update_display(200);
}

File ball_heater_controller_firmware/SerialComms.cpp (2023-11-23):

#include "SerialComms.h"

SerialComms::SerialComms(BallHeater *ball_heater)
{
    _ball_heater = ball_heater;
    _command_buffer_ptr = _command_buffer;
}

/*-------------------- tick -------------------------
      Reads available serial data into buffer and processes
      and executes if a full command has been recieved.
 ---------------------------------------------------------*/
void SerialComms::tick()
{
    // digitalWrite(8, HIGH);
    // read bytes available into buffer.
    while (Serial.available() > 0)
    {

        if (_command_write_pos == _command_read_pos - 1)
        {
            // Do not overwrite unread commands
            break;
        }

        // put sock messages in command buffer
        byte inByte = (byte)Serial.read();
        *(_command_buffer_ptr + _command_write_pos) = inByte;
        _command_write_pos++;

        if (_command_write_pos >= COMMAND_BUFFER_SIZE)
        {
            // Wrap around command buffer
            _command_write_pos = 0;
        }
    }
    this->get_serial_commands();
    // digitalWrite(8, LOW);
}

/*-------------------- get_serial_commands -------------------------
      Reads the received serial data off of _command_buffer and checks integrity.
      Fires command if full command has been received an passed integrity checks.
      Echos back original command in this case.
 ---------------------------------------------------------*/

void SerialComms::get_serial_commands()
{
    while (_command_write_pos != _command_read_pos && !_command_ready)
    {
        // check for command timeout.
        if (_command_verification != 0 &&
            ((millis() - _command_start_time) > COMMAND_READ_TIMEOUT))
        {
            _command_verification = 0;
            this->reset();
        }

        // Haven't read all command bytes and a full command hasn't been read
        bool shouldClear = false;
        switch (_command_verification)
        {
        // Pre payload verification
        case 0:
            if (254 == (uint8_t) * (_command_buffer_ptr + _command_read_pos))
            {
                _command_verification = 1;
                _command_start_time = millis();
                // Serial.println("case0");
            }
            else
            {
                shouldClear = true;
            }
            break;
        // Pre payload verification
        case 1:
            if (237 == (uint8_t) * (_command_buffer_ptr + _command_read_pos))
            {
                _command_verification = 2;
            }
            else
            {
                shouldClear = true;
            }
            break;

        // Get Command Code
        case 2:
            if (this->verify_command_code((uint8_t) * (_command_buffer_ptr + _command_read_pos)))
            {
                if (_num_arg_bytes > 0)
                    _command_verification = 3;
                else
                    _command_verification = 4;
            }
            else
            {
                shouldClear = true;
            }
            break;

        case 3:
            // Serial.println("case3");

            // Get all the arument inputs
            if (_placed_args_bytes < _num_arg_bytes)
            {
                _command_args[_placed_args_bytes] = (uint8_t) * (_command_buffer_ptr + _command_read_pos);
                _placed_args_bytes++;
            }
            if (_placed_args_bytes == _num_arg_bytes)
            {
                _command_verification = 4;
            }
            break;
        // Post payload verification
        case 4:
            if (190 == (uint8_t) * (_command_buffer_ptr + _command_read_pos))
            {
                _command_verification = 5;
            }
            else
            {
                shouldClear = true;
            }
            break;
        // Post payload verification
        case 5:
            if (173 == (uint8_t) * (_command_buffer_ptr + _command_read_pos))
            {
                _command_ready = true;
                _command_verification = 0;
            }
            else
            {
                shouldClear = true;
            }
            break;

        default:
            shouldClear = true;
            break;
        }
        // Advance Read position and wrap if needed.
        _command_read_pos++;
        if (_command_read_pos >= COMMAND_BUFFER_SIZE)
            _command_read_pos = 0;

        // If error, clear socket command object
        if (shouldClear)
        {
            _command_verification = 0;
            this->reset();
        }
    }
    if (_command_ready)
    {
        // Serial.println("firing command");
        int retval = (this->*_commmand_func)(_command_args);
        // TODO: check retval and do something.

        this->echo_command();
        this->reset();
    }
}

/*-------------------- verify_command_code -------------------------
      Verifies that the command code is a valid number and sets
      the relavent parameters.
 ---------------------------------------------------------*/
bool SerialComms::verify_command_code(uint8_t code)
{
    if (code < NUMCOMMANDS)
    {
        _current_command_code = code;
        _commmand_func = _func_map[code];
        _num_arg_bytes = _num_arg_bytes_map[code];
        return true;
    }
    else
        return false;
}

/*-------------------- reset -------------------------
       Resets the command verification system in case of error.
 ---------------------------------------------------------*/
void SerialComms::reset()
{
    _num_arg_bytes = 0;
    _placed_args_bytes = 0;
    _command_ready = false;

    for (int i = 0; i < COMMAND_ARG_BUF_SIZE; i++)
    {
        _command_args[i] = NULL;
    }
}

/*-------------------- echo_command -------------------------
      Echos the received command and argbytes over serial for verification.
 ---------------------------------------------------------*/
void SerialComms::echo_command()
{
    Serial.write(0xFE);
    Serial.write(0xED);
    Serial.write(_current_command_code);
    Serial.write(_command_args, _placed_args_bytes);
    Serial.write(0xBE);
    Serial.write(0xAD);
}

/*-------------------- send_status -------------------------
       Return the current temperatures and setpoints via serial.
 ---------------------------------------------------------*/
int SerialComms::send_status(byte *in_byte)
{
    write_float(_ball_heater->get_target_temp());
    write_float(_ball_heater->get_pwm_float());
    write_float(_ball_heater->get_heater_temp());
    write_float(_ball_heater->get_aux_therm_temp());
    Serial.write(_ball_heater->get_control_mode());
    return 0;
}
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

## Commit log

2023-10-19 Initial Commit. PCB V1 ordered
    [ball_heater_controller-B_Cu.gbr, ball_heater_controller-B_Mask.gbr, ball_heater_controller-B_Paste.gbr, ball_heater_controller-B_Silkscreen.gbr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]
2023-10-20 adjusted PCB, added no-reset switch
    [ball_heater_controller-B_Cu.gbr, ball_heater_controller-B_Mask.gbr, ball_heater_controller-B_Paste.gbr, ball_heater_controller-B_Silkscreen.gbr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]
2023-10-30 initial commit of ROS node etc for ball heater
2023-11-10 added no temp sensor error fixed string parsing and backlight
2023-11-21 changed to porportional on measurement and updated some thingsn
    [ball_heater_controller.kicad_sch]
2023-11-22 added filter based non-responsive safety error.
2023-12-04 added gui node to control and monitor the heater
2023-12-05 added BOM and updated docs
    [ball_heater_controller_bom_.csv, ball_heater_controller_bom_V 1.ods]
2023-12-05 added enclosure files
2023-12-05 updated BOM
    [ball_heater_controller_bom_V 1.ods]
2023-12-08 updated assembly instructions and BOM
    [ball_heater_controller_bom_V 1.ods]
2023-12-08 updated assembly and added new enclosure
2023-12-14 updated BOM and printout
    [ball_heater_controller_bom_V 1.ods]
2023-12-21 updated assembly instructions
2024-01-25 Adjusted heater firmware settings. Programming first batch of controllers!
2024-01-26 added PCB pdf
    [ball_heater_controller.kicad_pcb]
2024-02-05 updated readme assembly instructions
    [ball_heater_guide-01.stl]
2024-02-06 updated enclosure
2024-05-21 fixed wire length
2025-06-24 updated wire length / fuse size
